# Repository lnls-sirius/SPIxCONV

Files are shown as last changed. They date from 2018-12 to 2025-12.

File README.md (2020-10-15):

# SPIxCONV

This project consists of an 18-bit analog input (ADC) and output (DAC) within a range of 20 V (± 10 V) and 32 digital pins that can be either as inputs or outputs. This system interfaces with pulsed power electronics hardware in order to control the output voltage for pulsed magnets as well as read and write status commands to their power supplies. An operator interface (OPI) software based on Qt was also developed for remote control.

<!--========================================-->
## Hardware
<!--========================================-->

<!--==============================-->
### Main Board
<!--==============================-->

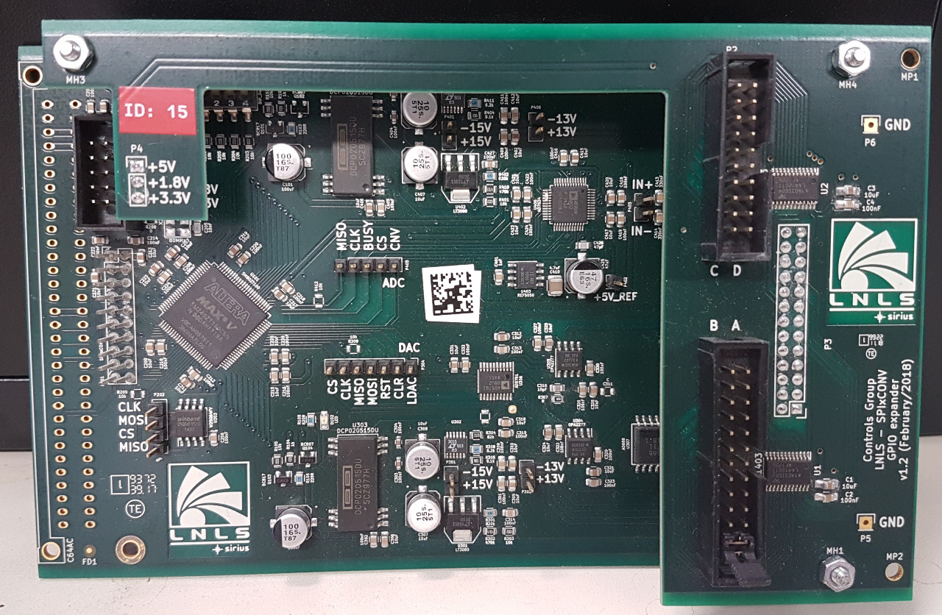
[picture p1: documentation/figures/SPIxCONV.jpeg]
Main Board


<!--====================-->
#### Circuit
<!--====================-->

  - Board
<p float="left">
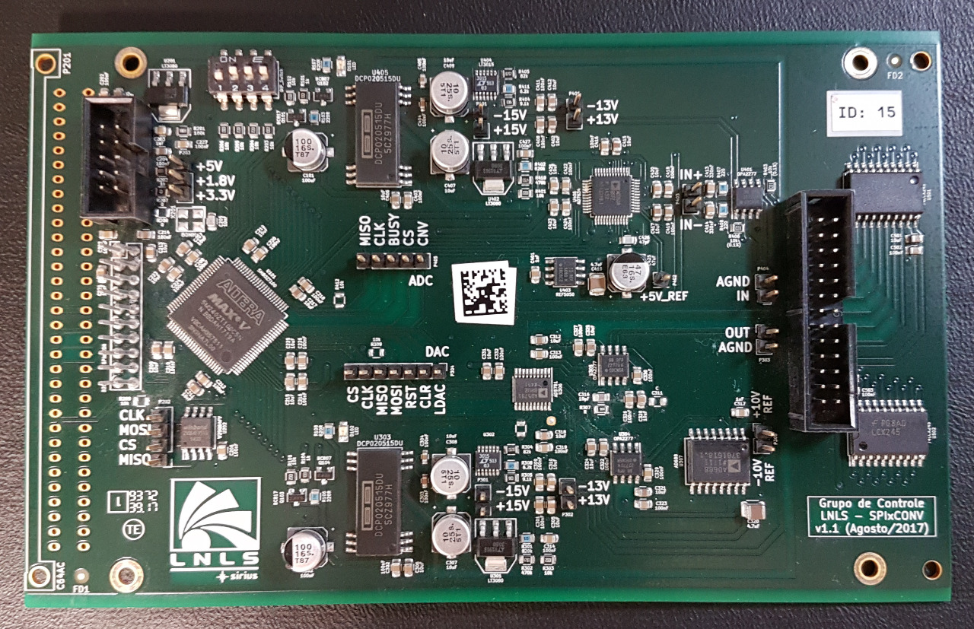
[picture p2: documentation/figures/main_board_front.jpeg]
  
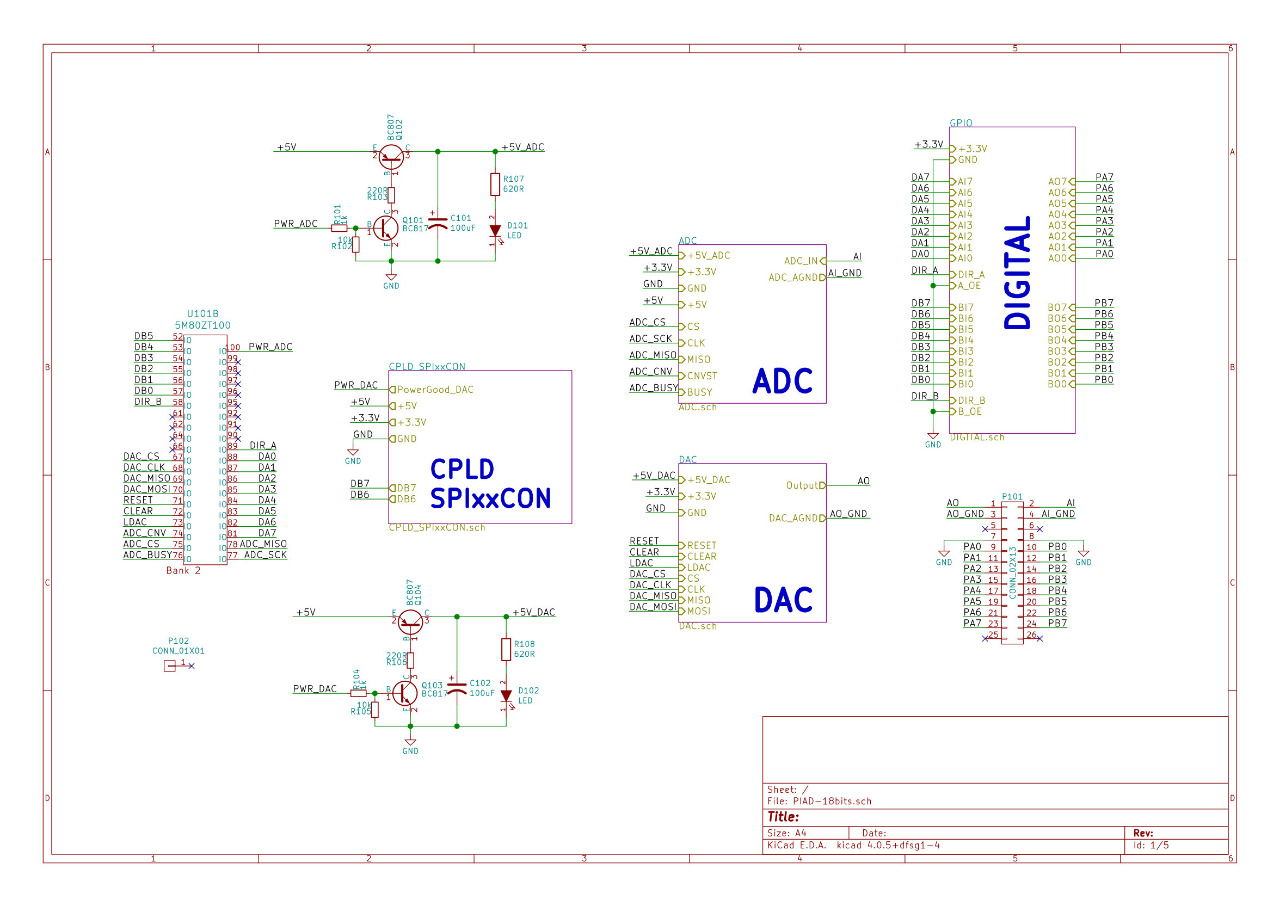
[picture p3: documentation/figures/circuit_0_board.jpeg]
   
</p>

  - CPLD
<p float="left">
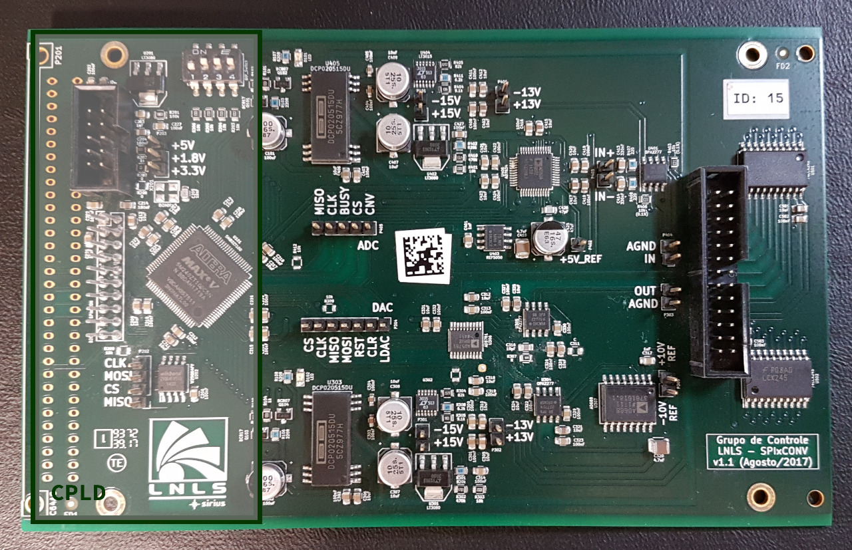
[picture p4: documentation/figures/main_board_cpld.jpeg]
  
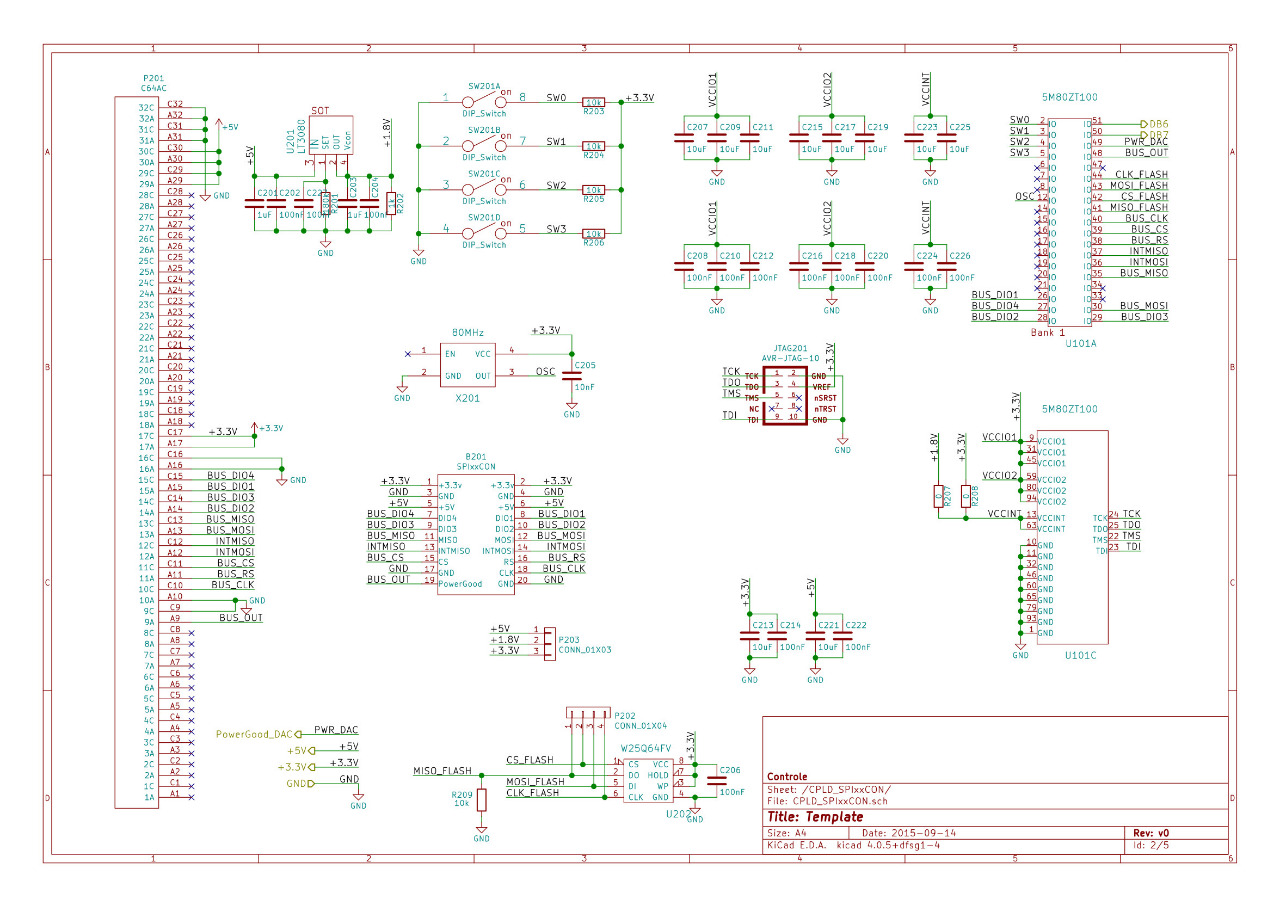
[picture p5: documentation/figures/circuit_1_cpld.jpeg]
   
</p>

  - DAC
<p float="left">
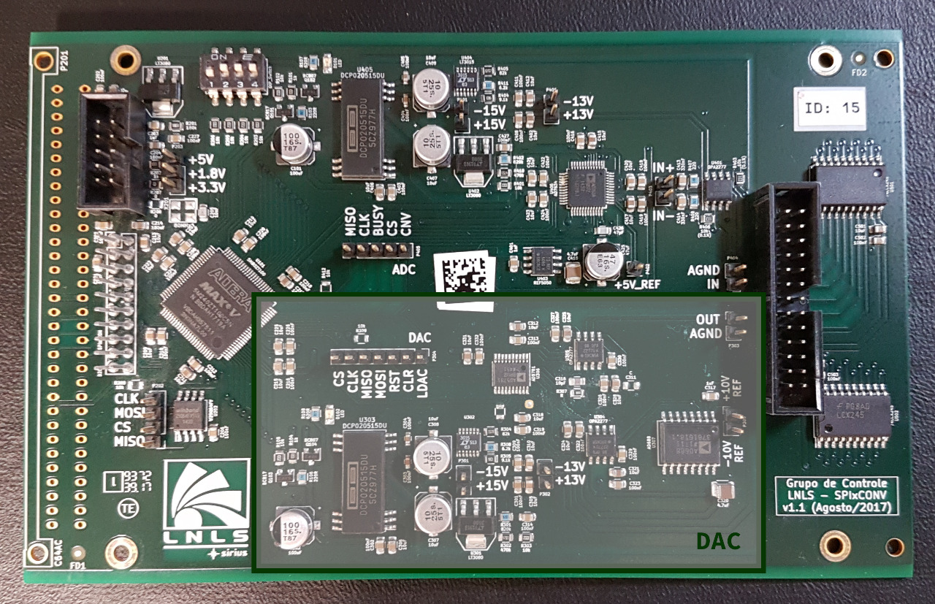
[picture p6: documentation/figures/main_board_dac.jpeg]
  
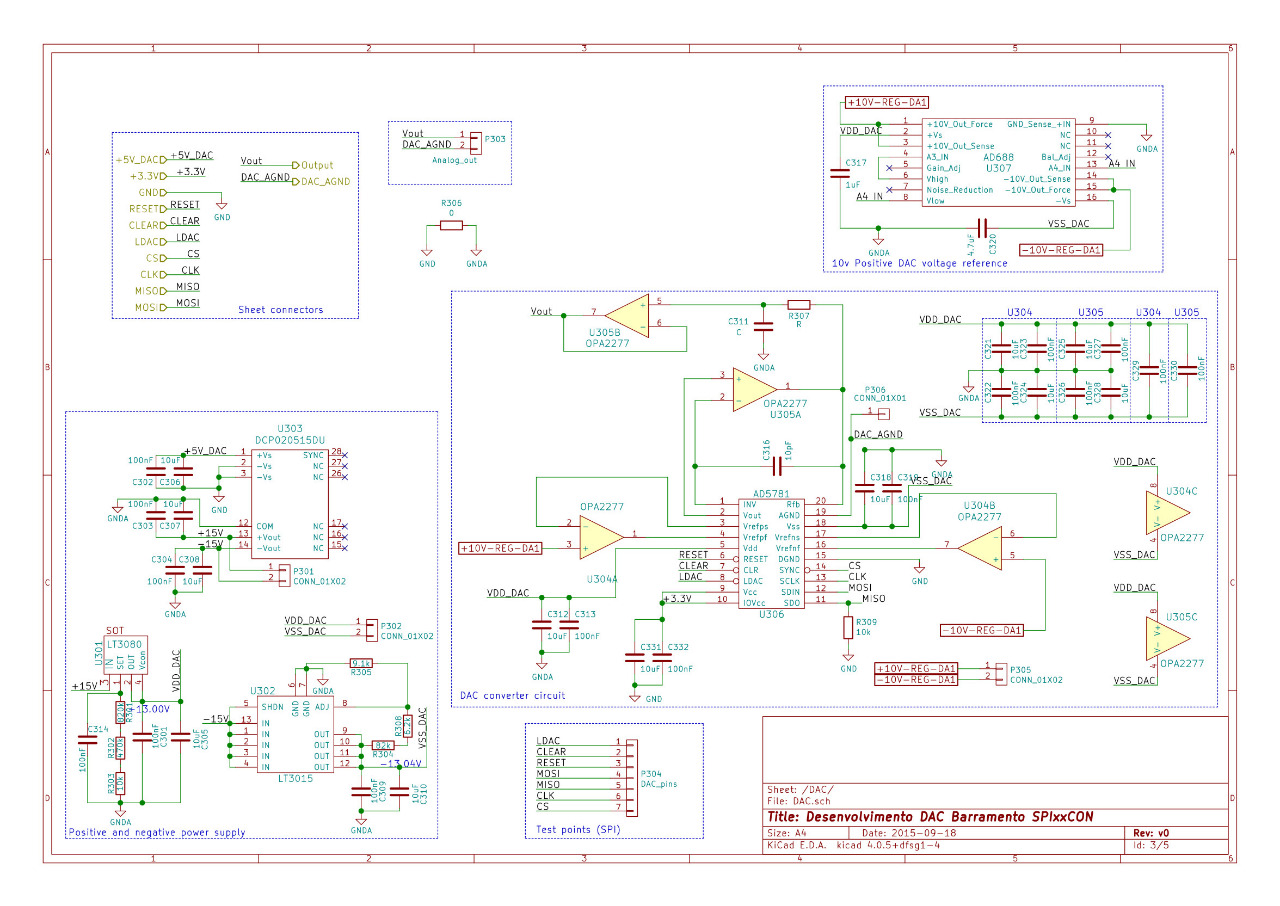
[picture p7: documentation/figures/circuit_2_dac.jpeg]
   
</p>

  - ADC
<p float="left">
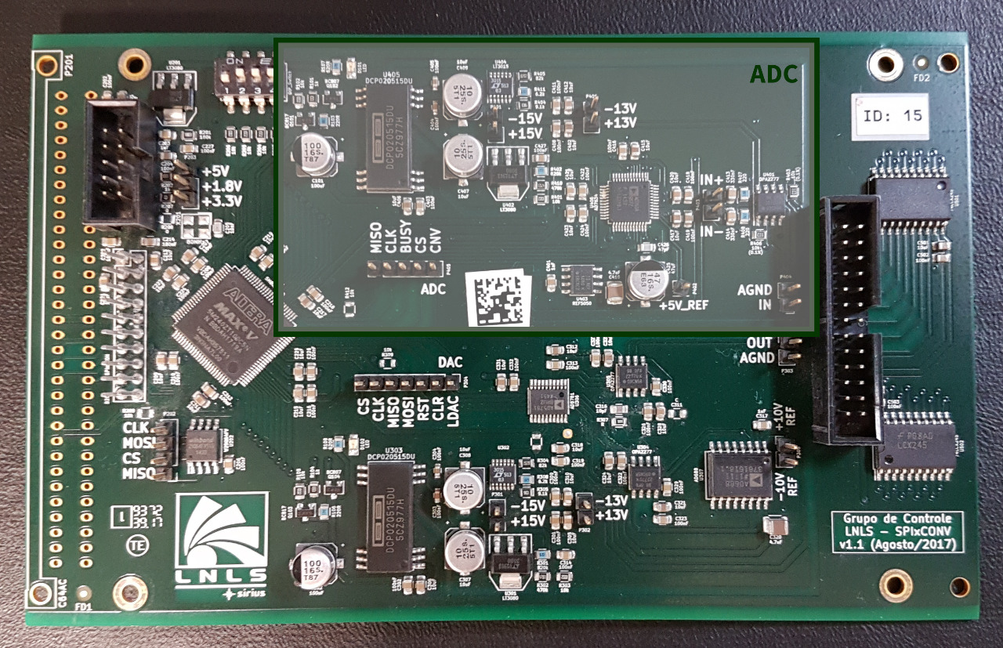
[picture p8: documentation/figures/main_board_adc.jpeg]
  
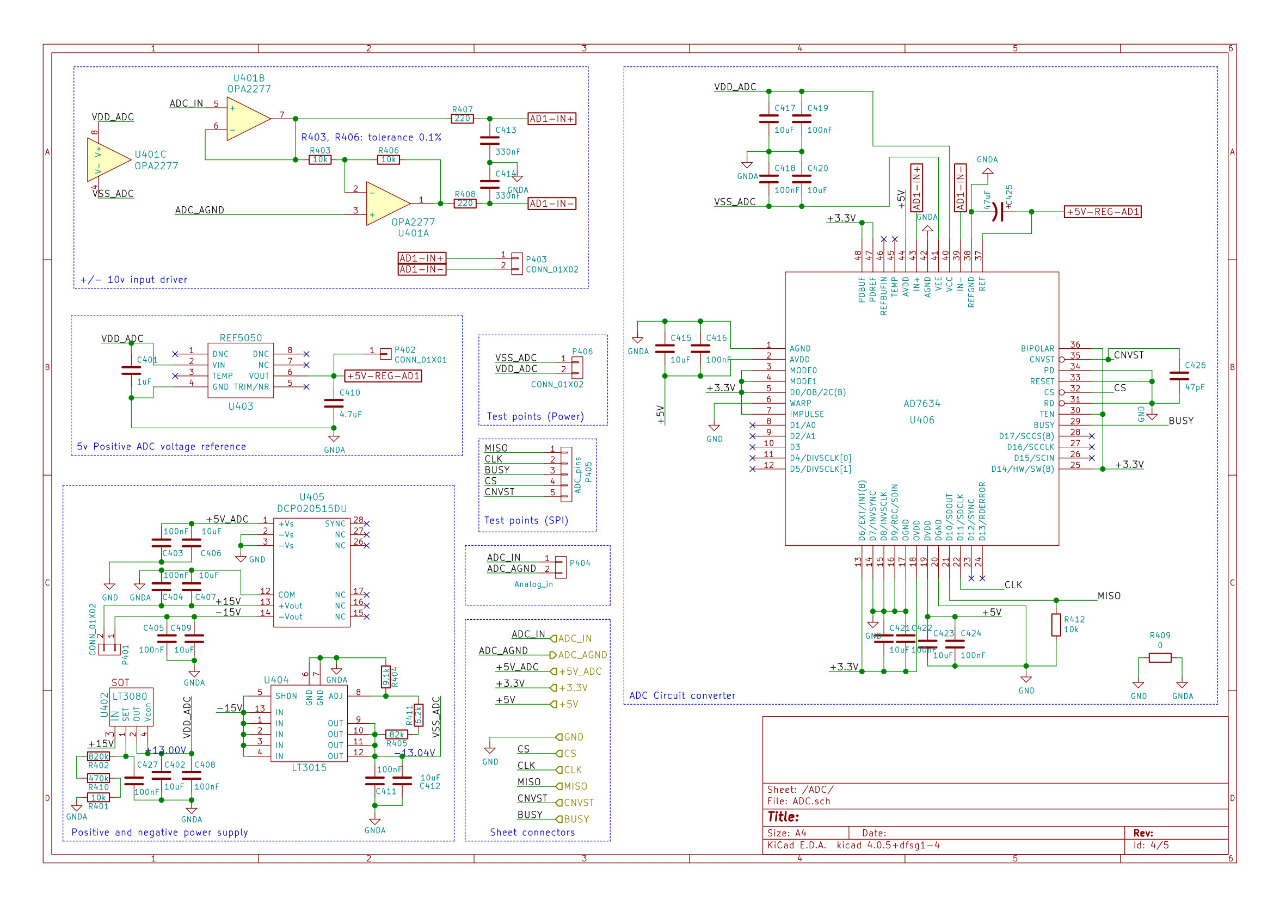
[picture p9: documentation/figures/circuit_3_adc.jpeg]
   
</p>

  - Digital I/O
<p float="left">
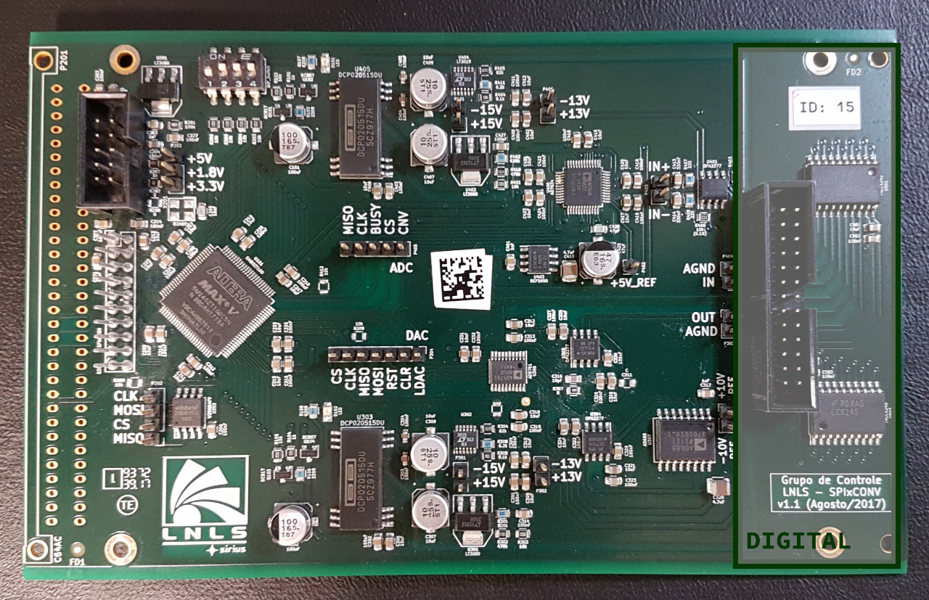
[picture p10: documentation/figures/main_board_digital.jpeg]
  
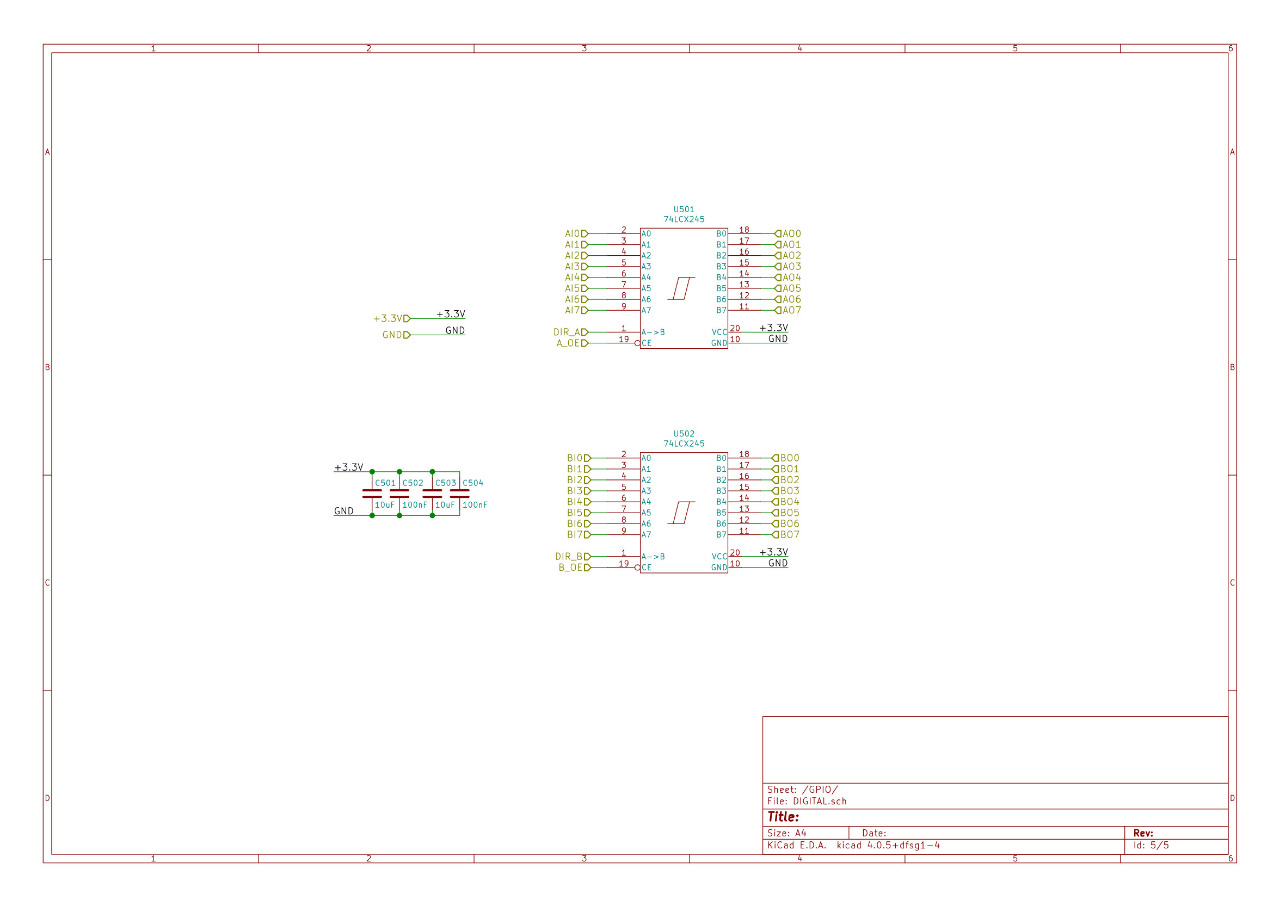
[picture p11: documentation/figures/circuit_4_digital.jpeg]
   
</p>

<!--====================-->
#### PCB
<!--====================-->

<p float="left">
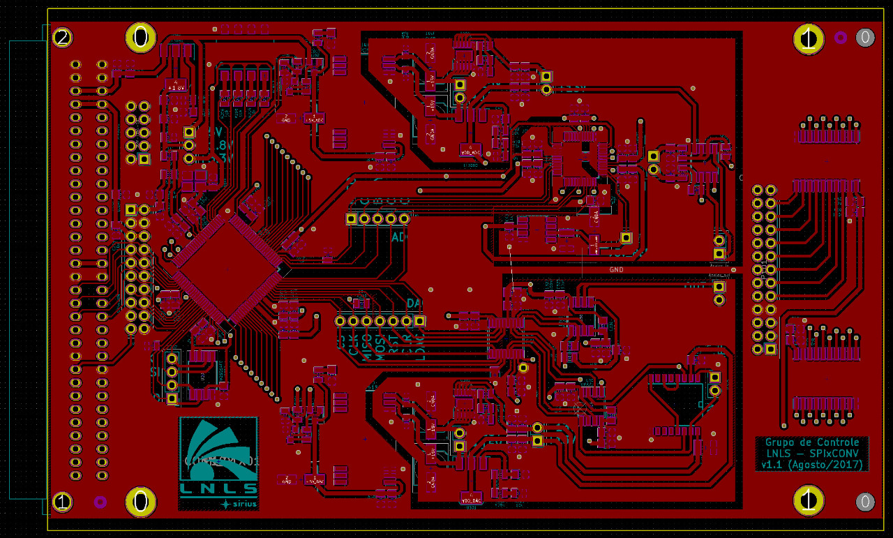
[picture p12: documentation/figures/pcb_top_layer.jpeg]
   
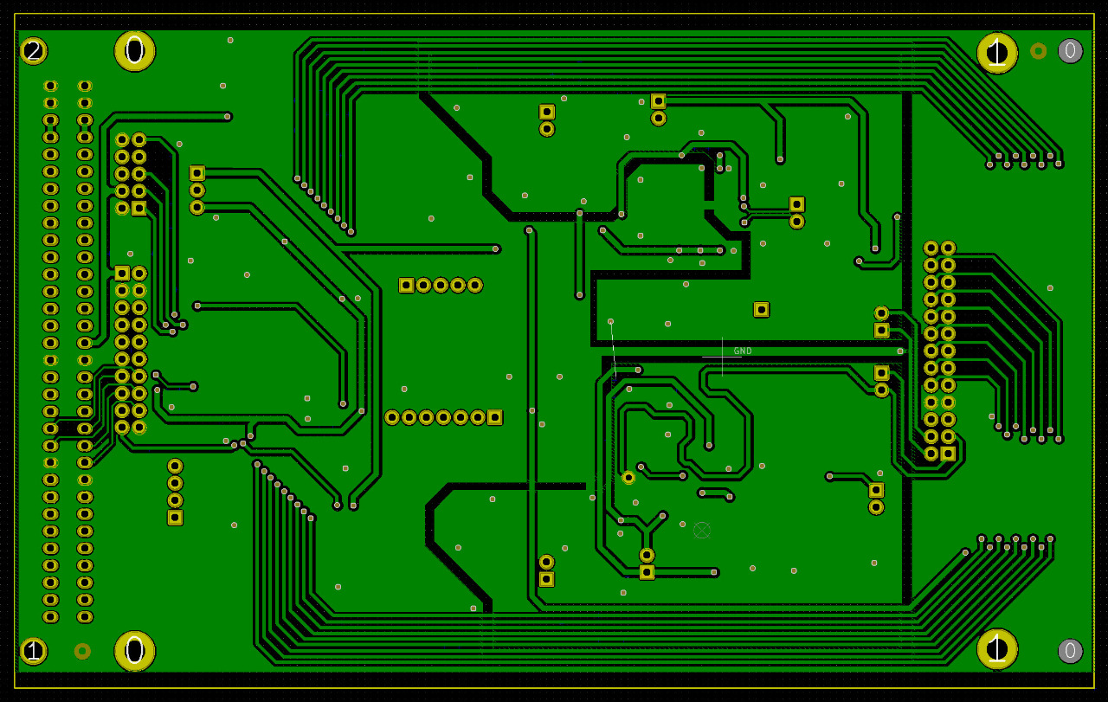
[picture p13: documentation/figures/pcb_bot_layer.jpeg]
  
</p>

<!--====================-->
#### Connectors
<!--====================-->

  - SPIxxCON
<p float="left">
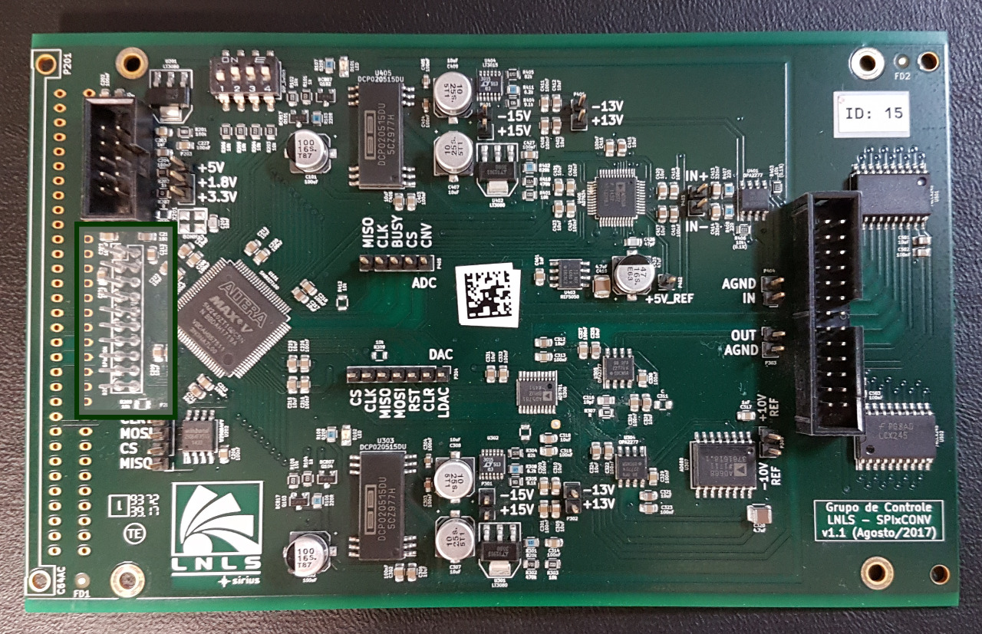
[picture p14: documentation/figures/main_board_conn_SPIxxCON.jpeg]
   
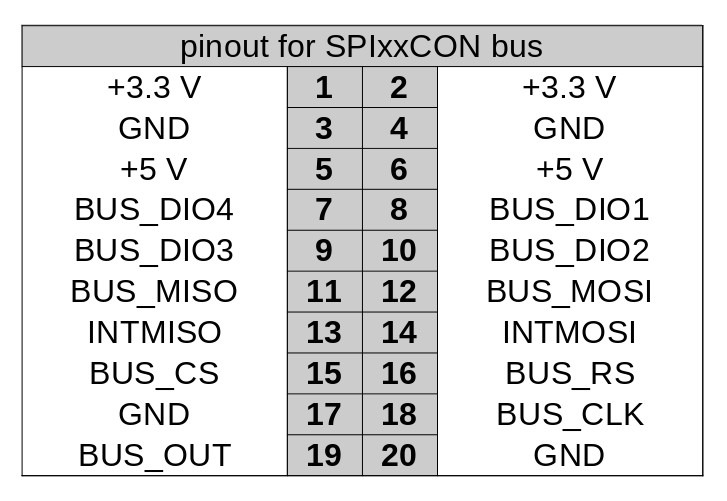
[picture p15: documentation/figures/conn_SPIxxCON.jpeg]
  
</p>

  - CPLD
<p float="left">
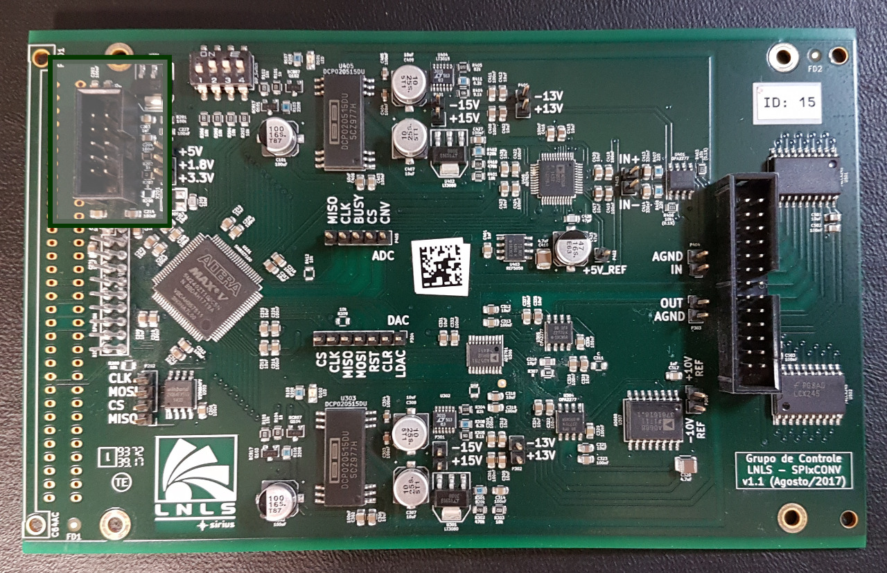
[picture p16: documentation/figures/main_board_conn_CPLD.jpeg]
   
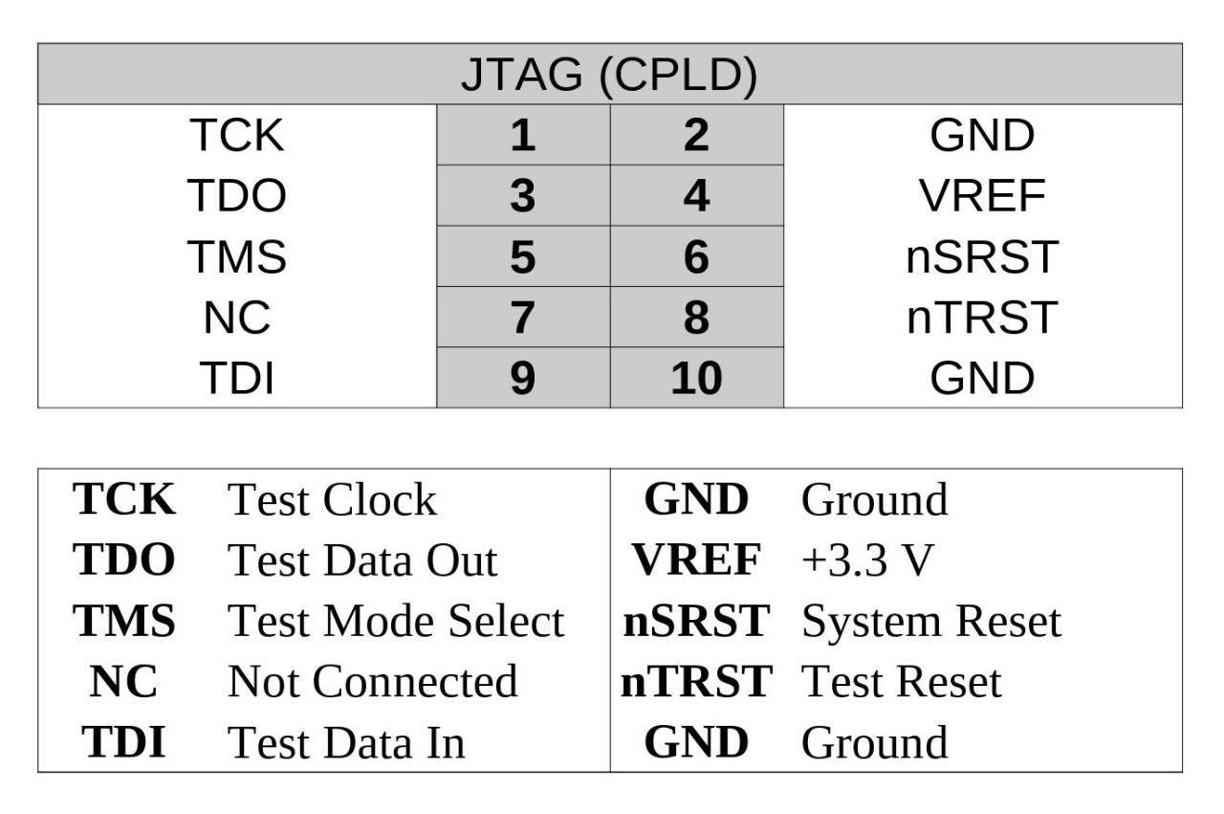
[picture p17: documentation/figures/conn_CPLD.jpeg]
  
</p>

  - Board Connection Link
<p float="left">
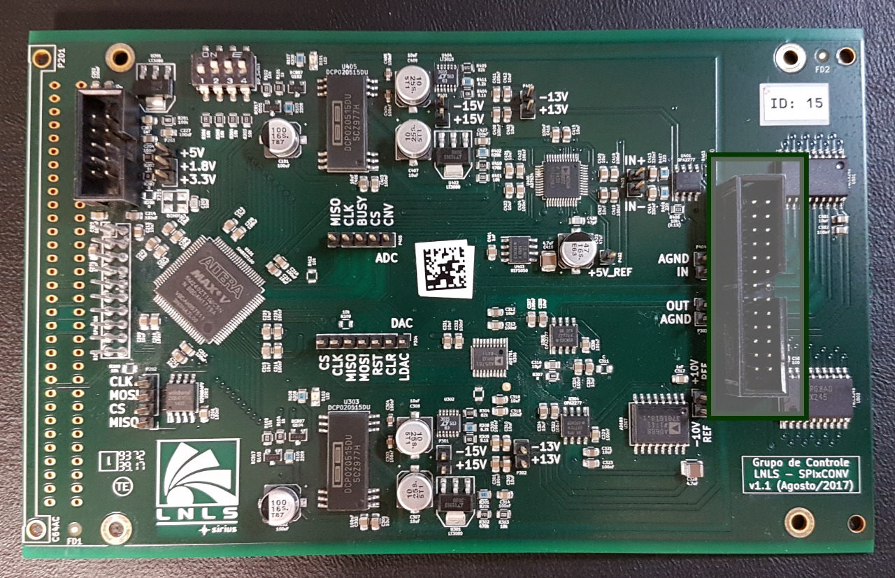
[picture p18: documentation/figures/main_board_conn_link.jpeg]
   
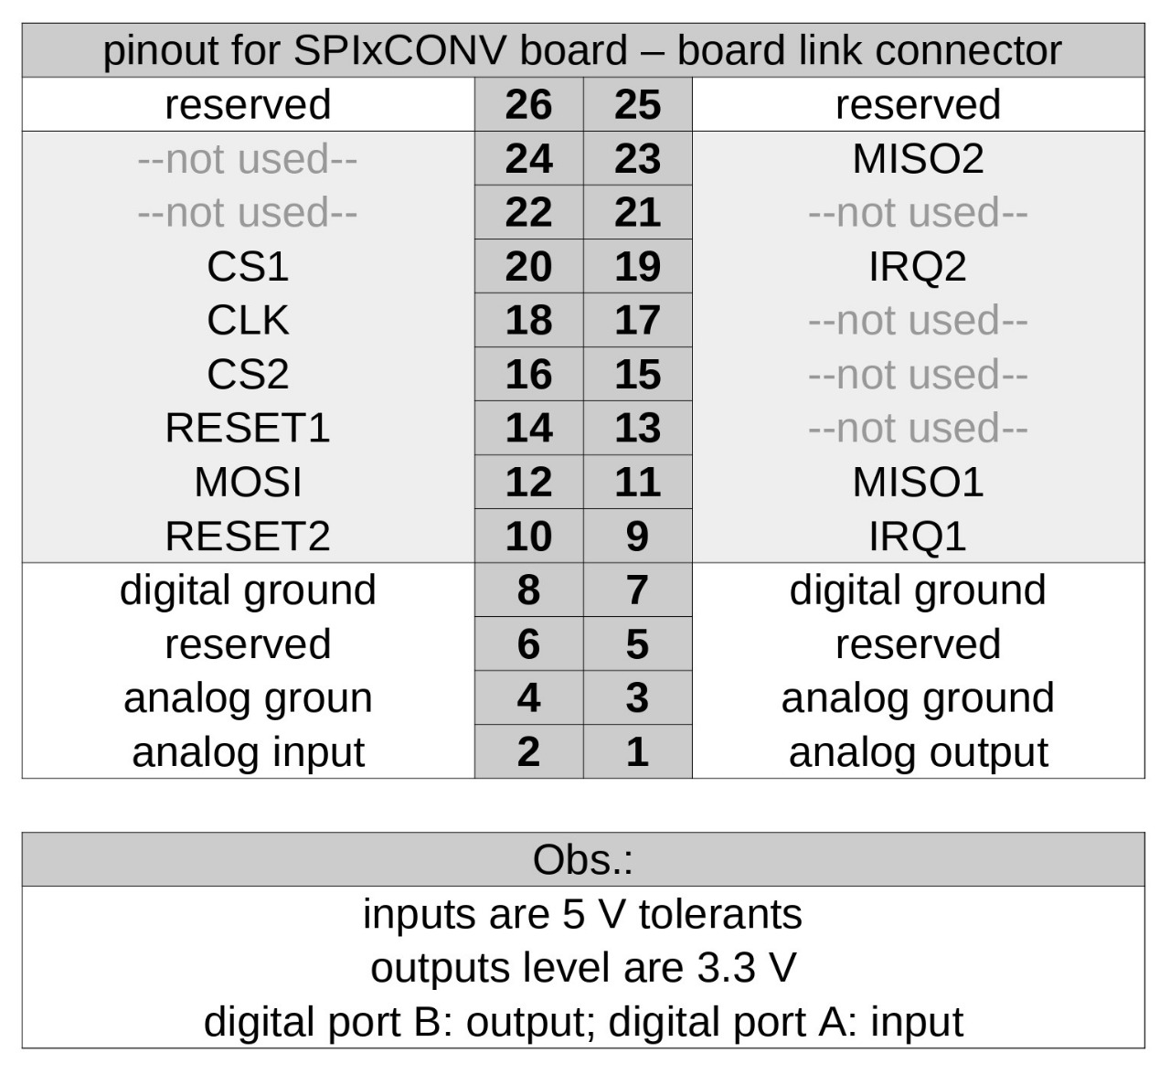
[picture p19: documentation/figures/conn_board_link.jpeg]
  
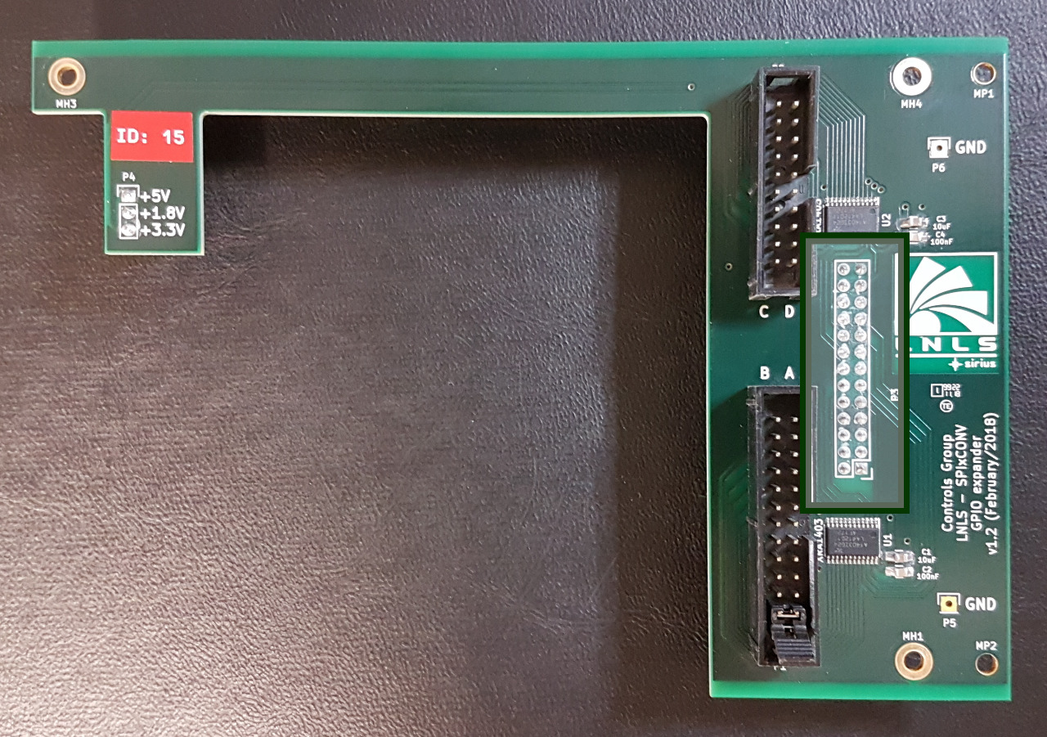
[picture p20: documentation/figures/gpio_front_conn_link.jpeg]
  
</p>

<!--====================-->
#### Test Points
<!--====================-->

  - SPI
<p float="left">
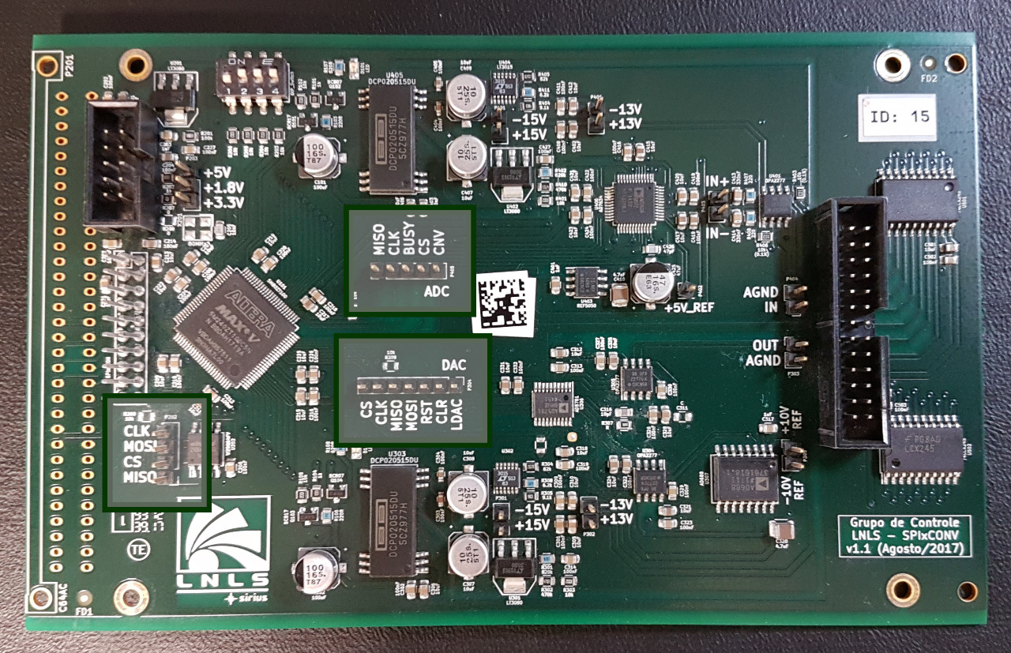
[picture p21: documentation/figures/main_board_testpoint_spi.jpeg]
  
</p>

  - Power Voltage
<p float="left">
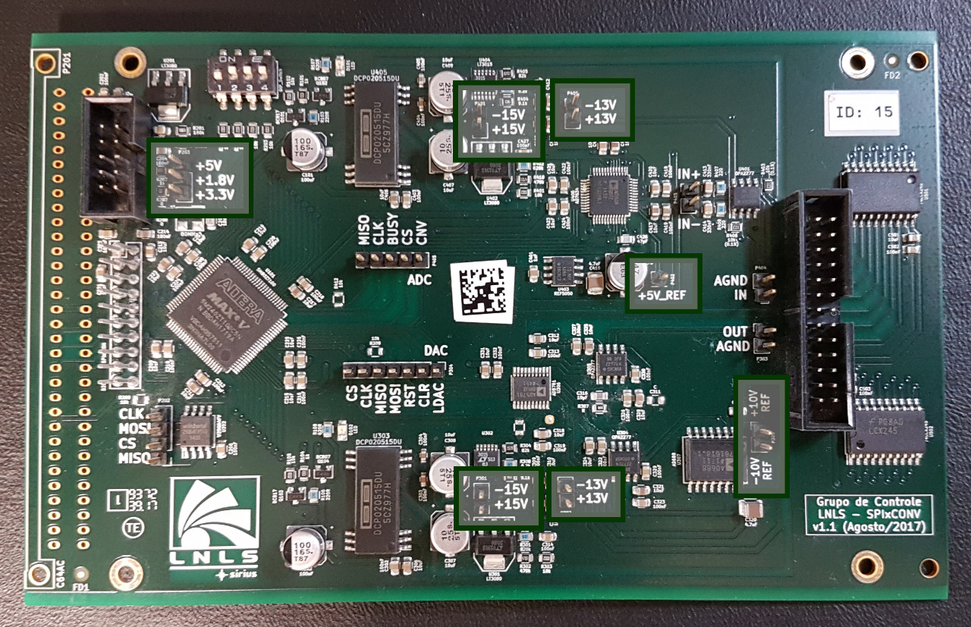
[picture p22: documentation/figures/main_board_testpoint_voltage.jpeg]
  
</p>

  - Analog In/Out
<p float="left">
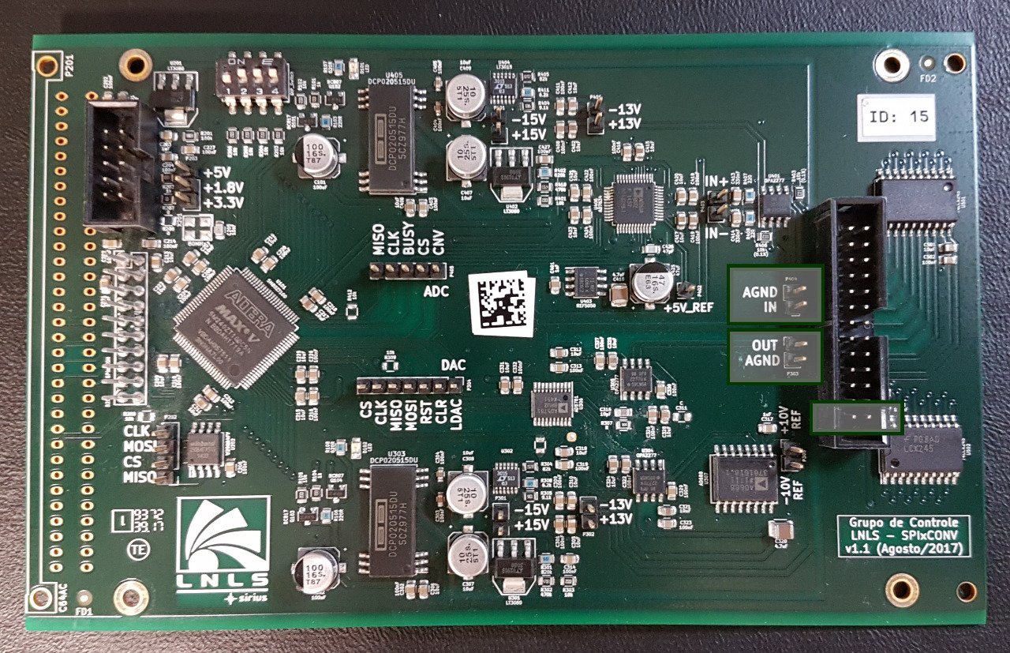
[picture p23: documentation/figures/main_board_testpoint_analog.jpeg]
  
</p>

<!--====================-->
#### BOM
<!--====================-->
Bill of materials

<!--==============================-->
### GPIO Expander Board
<!--==============================-->

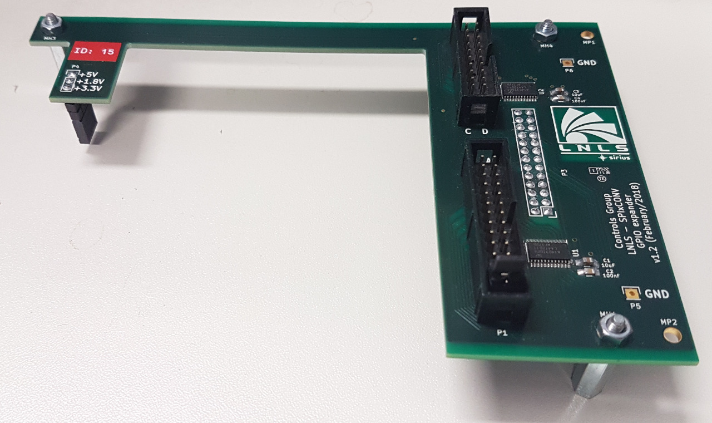
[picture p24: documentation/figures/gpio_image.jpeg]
GPIO Expander Board


<!--====================-->
#### Circuit
<!--====================-->
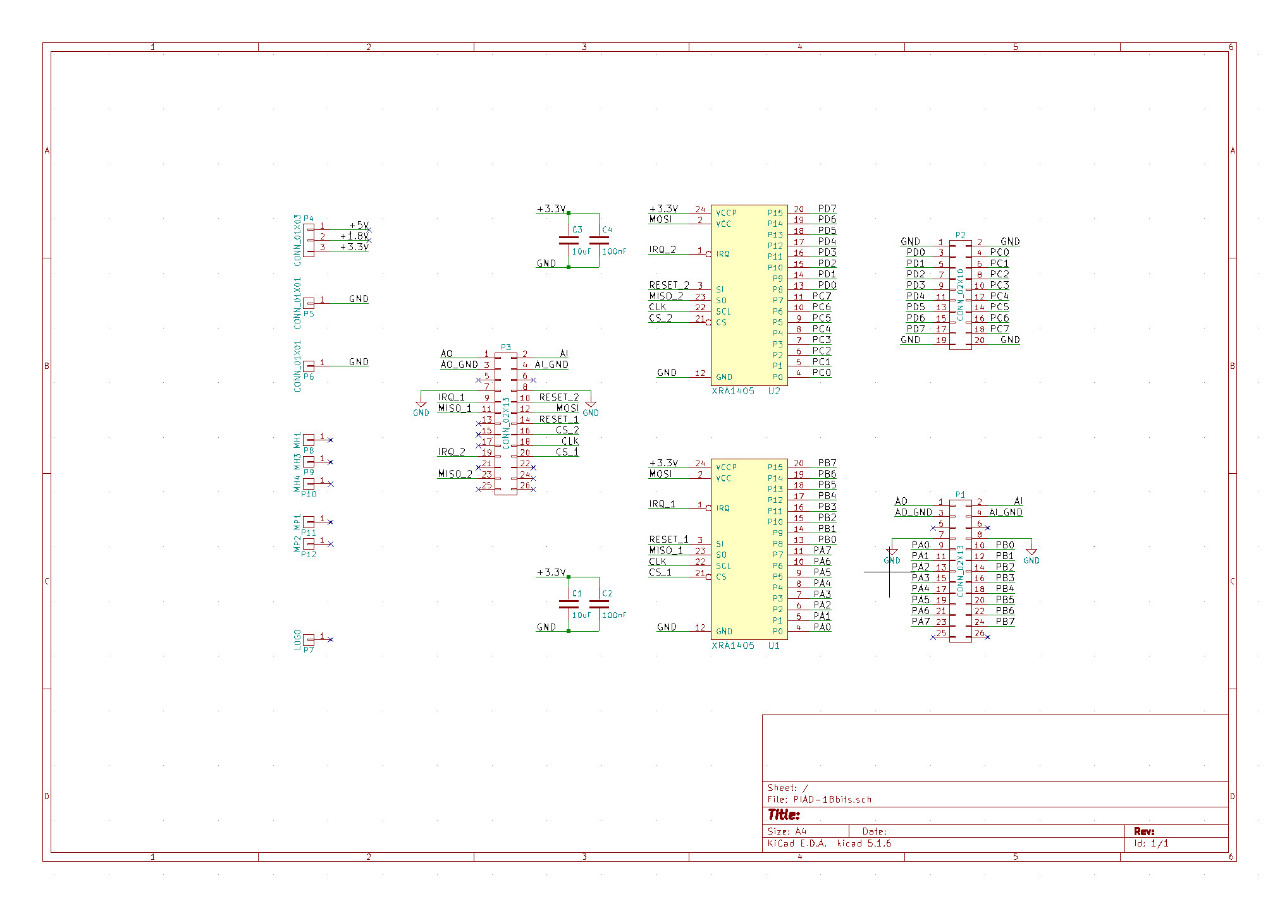
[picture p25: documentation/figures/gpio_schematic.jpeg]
GPIO board circuit


<!--====================-->
#### PCB
<!--====================-->
<p float="left">
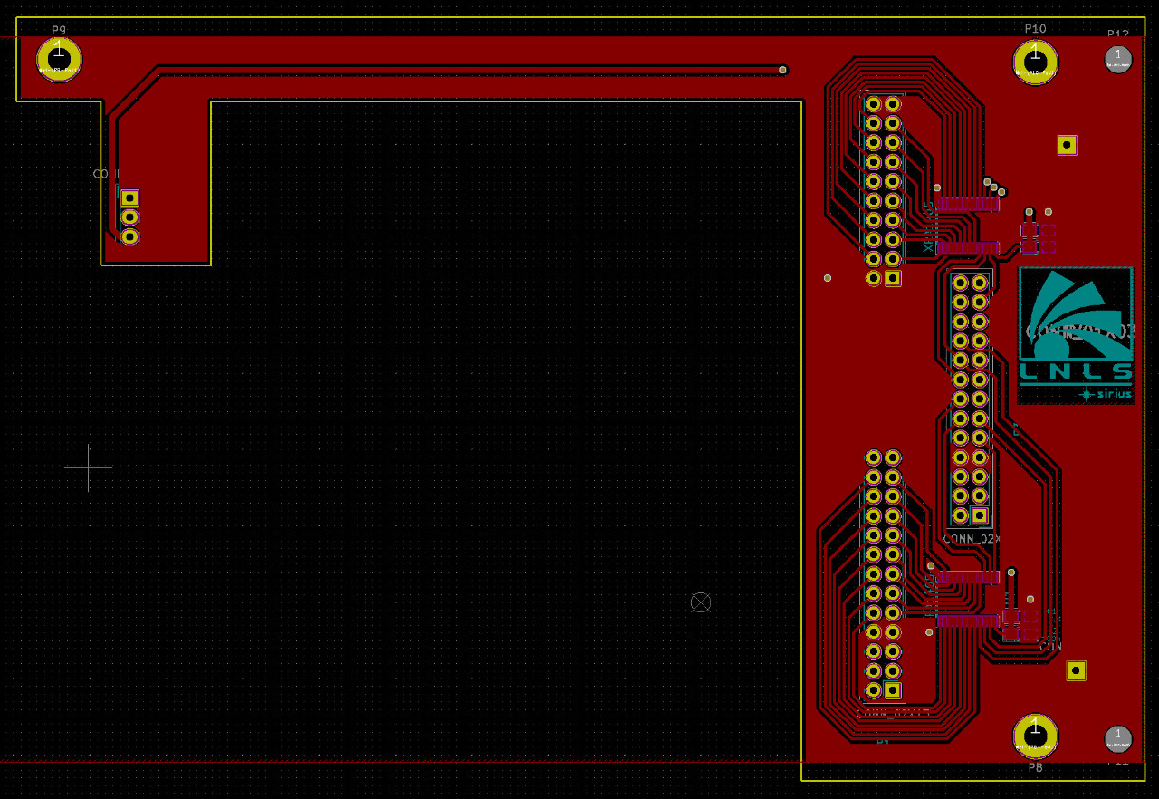
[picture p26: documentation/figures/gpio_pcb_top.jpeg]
   
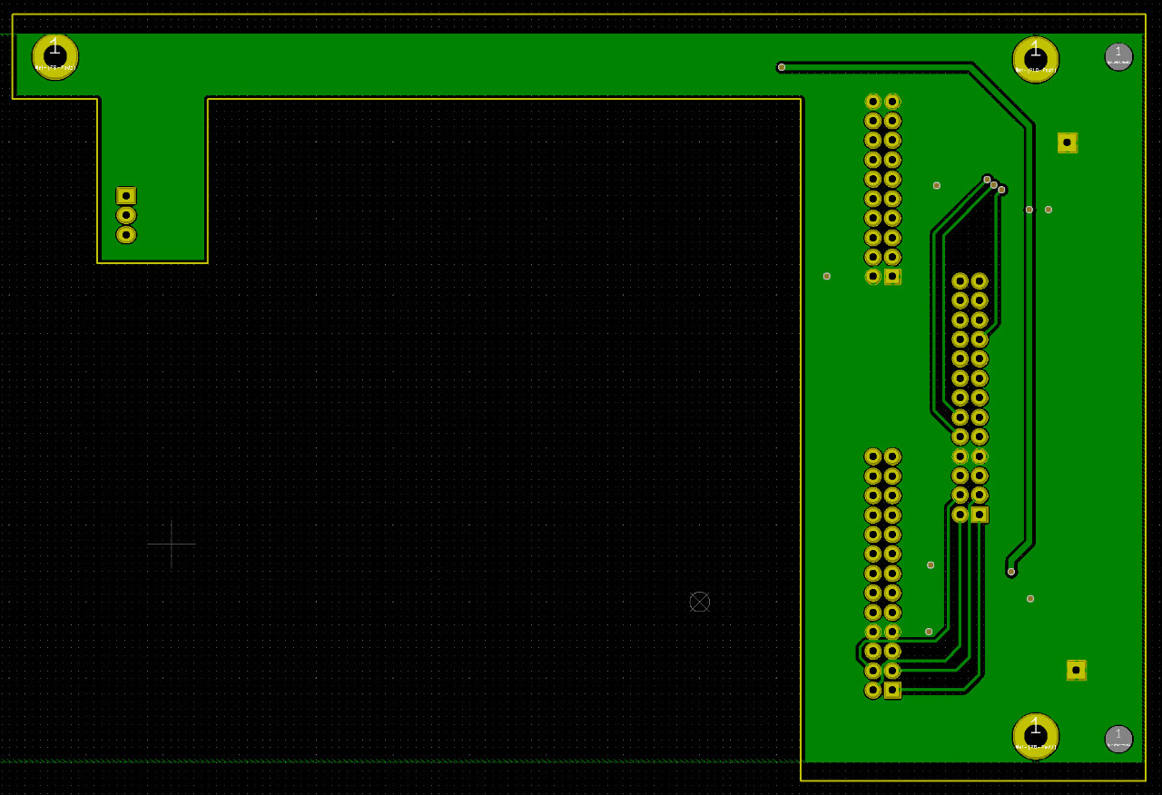
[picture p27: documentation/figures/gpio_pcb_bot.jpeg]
  
</p>

<!--====================-->
#### Connectors
<!--====================-->

  - Interface A/B
<p float="left">
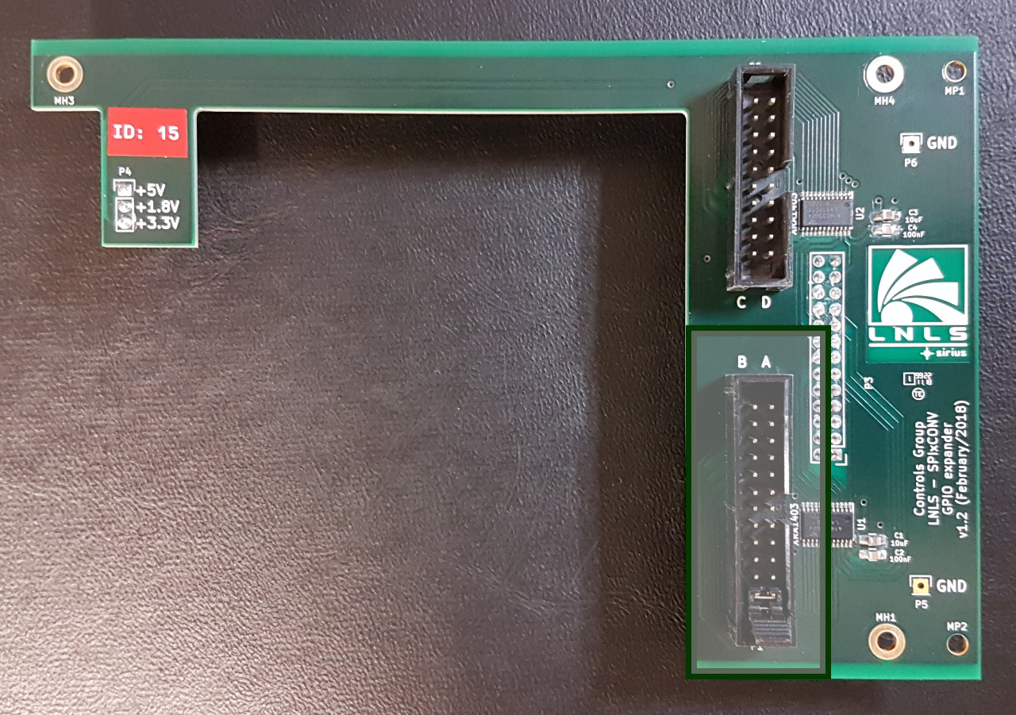
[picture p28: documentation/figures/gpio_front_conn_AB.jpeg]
   
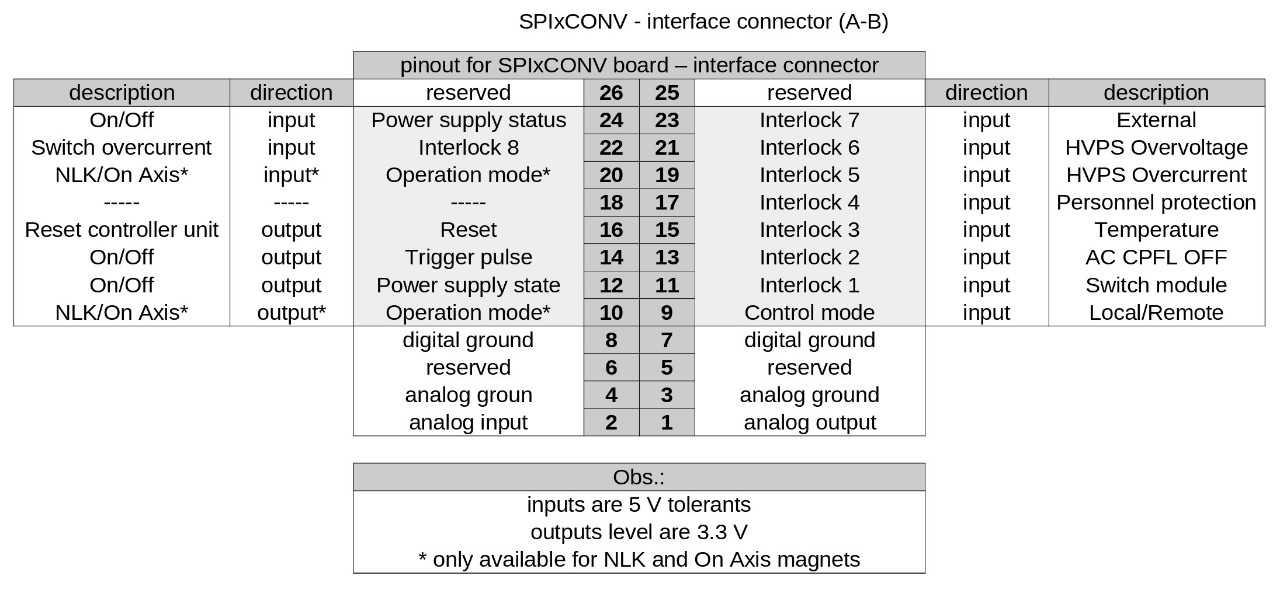
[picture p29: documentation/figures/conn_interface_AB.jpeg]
  
</p>

  - Interface C/D
<p float="left">
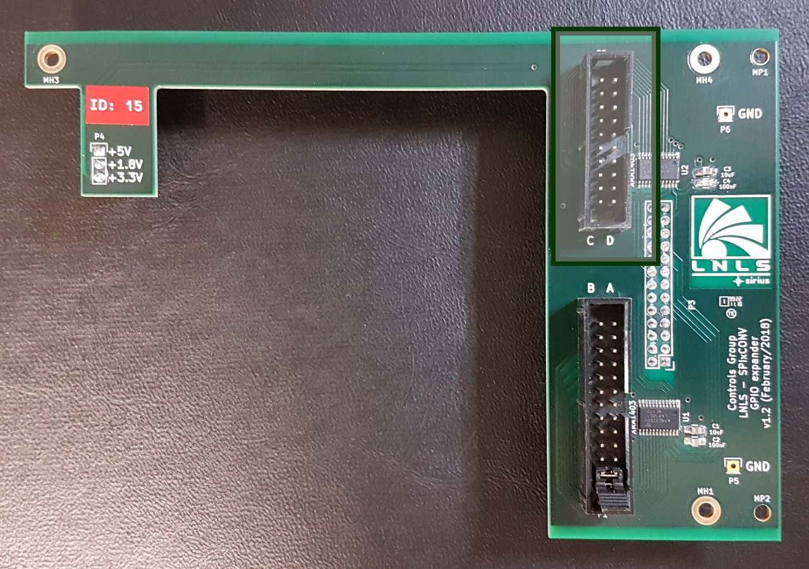
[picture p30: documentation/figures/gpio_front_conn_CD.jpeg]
   
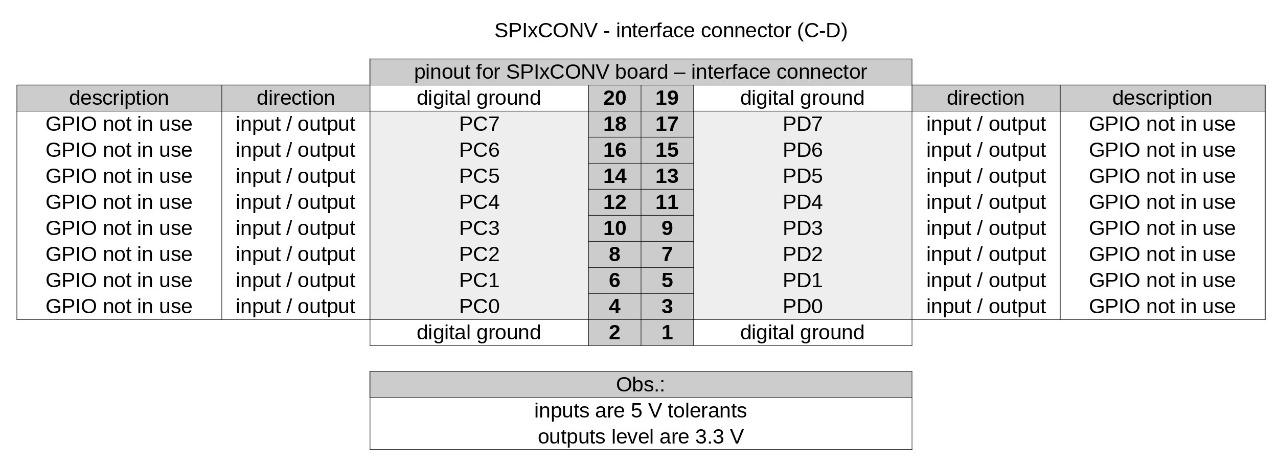
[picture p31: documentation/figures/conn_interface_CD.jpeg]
  
</p>

<!--====================-->
#### Test Points
<!--====================-->

  - Power Voltage
<p float="left">
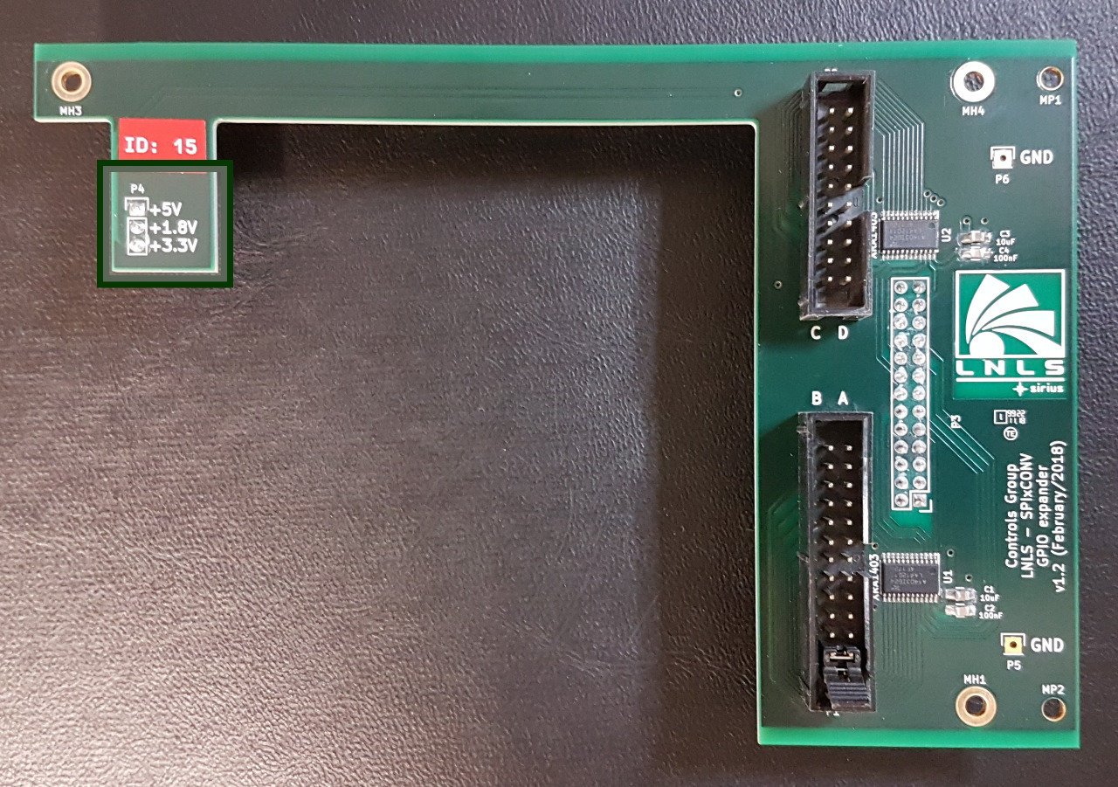
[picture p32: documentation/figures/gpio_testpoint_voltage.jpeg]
  
</p>

  - Analog In/Out
<p float="left">
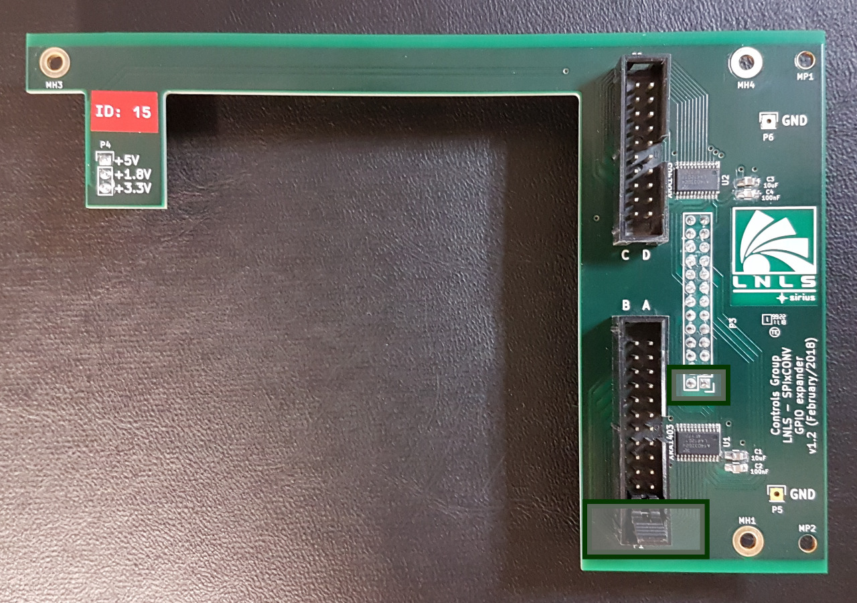
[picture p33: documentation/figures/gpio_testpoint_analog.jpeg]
  
</p>

<!--====================-->
#### BOM
<!--====================-->
Bill of materials

<!--====================-->
### Identification
<!--====================-->
<p float="left">
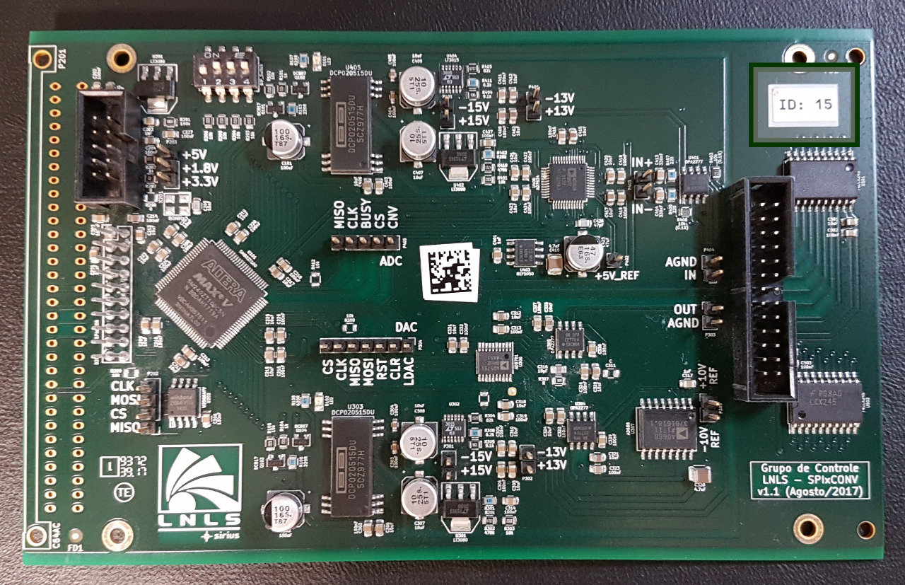
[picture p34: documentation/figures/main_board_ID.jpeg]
   
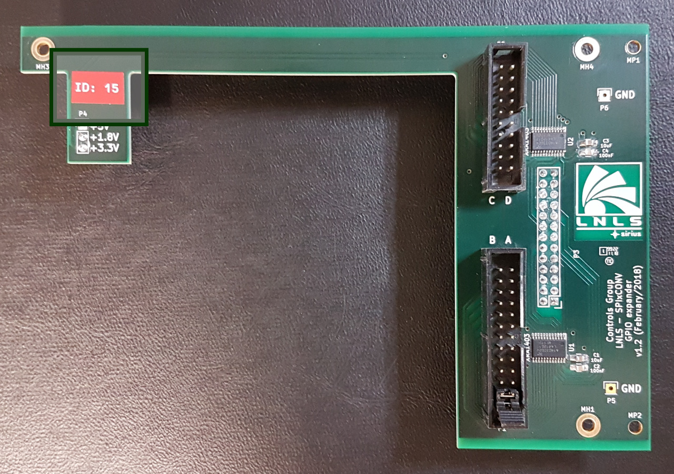
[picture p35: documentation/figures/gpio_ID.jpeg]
  
</p>

<!--========================================-->
### Software
<!--========================================-->

The software files of this project related to the server-side (IOC) is now available at [streamdevice-ioc](https://github.com/lnls-sirius/streamdevice-ioc) GitHub's repository under the "spixconv" directory.

The software files related to the OPI (Operator Interface) is now at [pydm-opi](https://github.com/lnls-sirius/pydm-opi) GitHub's repository.

Finally, the client-side (Python code) is at this repository under the [scripts](https://github.com/lnls-sirius/SPIxCONV/tree/master/software/scripts) directory.

<!--====================-->
#### Brief Description
<!--====================-->
To remotely control the board an [EPICS](https://epics-controls.org/about-epics/) IOC with an OPI was developed.

The IOC was built using [asynDriver](https://epics.anl.gov/modules/soft/asyn/) and [StreamDevice](http://epics.web.psi.ch/software/streamdevice/) on top of it. The application is launched in a form of a Docker container. The Docker image can be found at [Docker Hub](https://hub.docker.com/repository/docker/lnlscon/streamdevice-ioc) with the tag "SPIxCONV" followed by the version (eg: SPIxCONV-v1.9.6).

To configure the parameters of the IOC a [spreadsheet](https://cnpemcamp.sharepoint.com/:x:/s/controle/EUG0_4JUaz9Au7kZNcMZwZQB1x5OJBN_1QMdbbCGJ1Driw?e=Po8LNr) is used (available for CNPEM accounts only). PV's prefix, Power Supply voltage, host IP to connect to, scan rate and other settings can be adjusted. 

<!--====================-->
#### OPI (Operator Interface)
<!--====================-->

Previously, [Control System Studio](http://controlsystemstudio.org/) was used to develop the OPI. The windows can still be found under the [CSS](https://github.com/lnls-sirius/SPIxCONV/tree/master/software/CSS) directory. Lately, we have been using [PyDM (Python Display Manager)](https://slaclab.github.io/pydm/) to develop the windows. As stated before, the files related to the PyDM OPI is located in [pydm-opi](https://github.com/lnls-sirius/pydm-opi) repository.

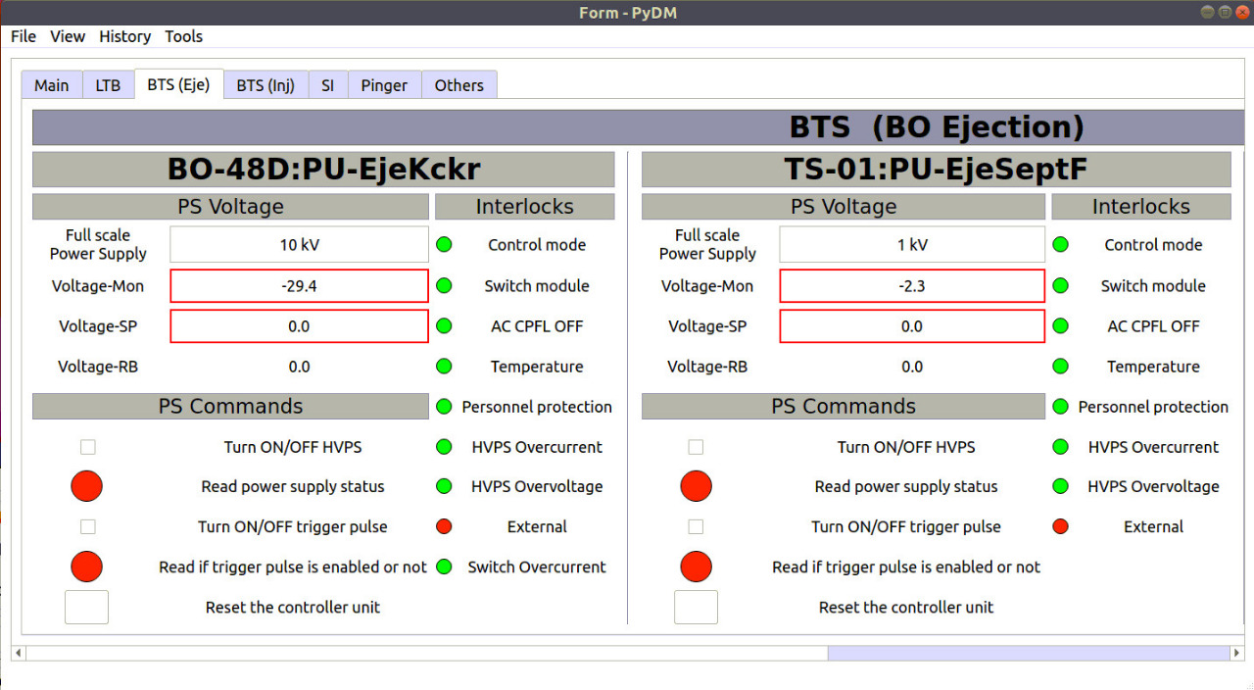
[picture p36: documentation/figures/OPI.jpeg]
OPI


<!--====================-->
#### CPLD
<!--====================-->

<p float="left">
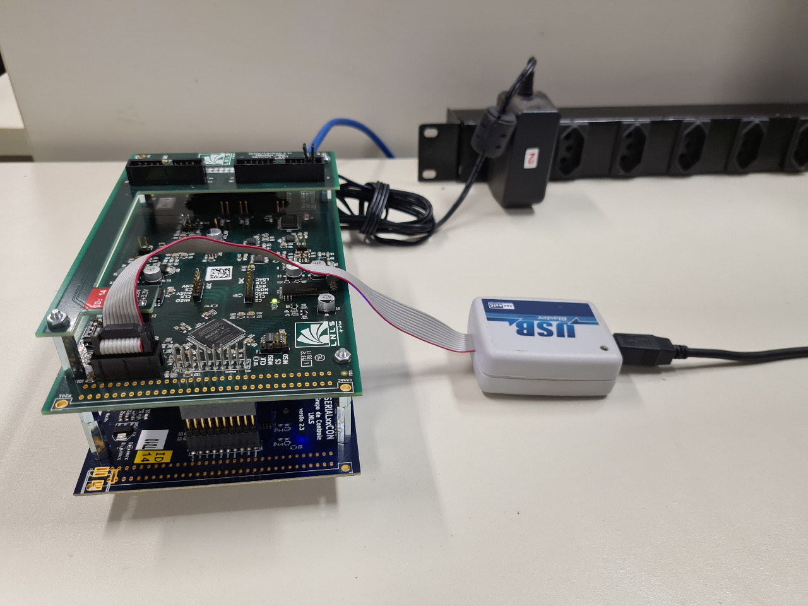
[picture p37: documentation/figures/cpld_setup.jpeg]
   
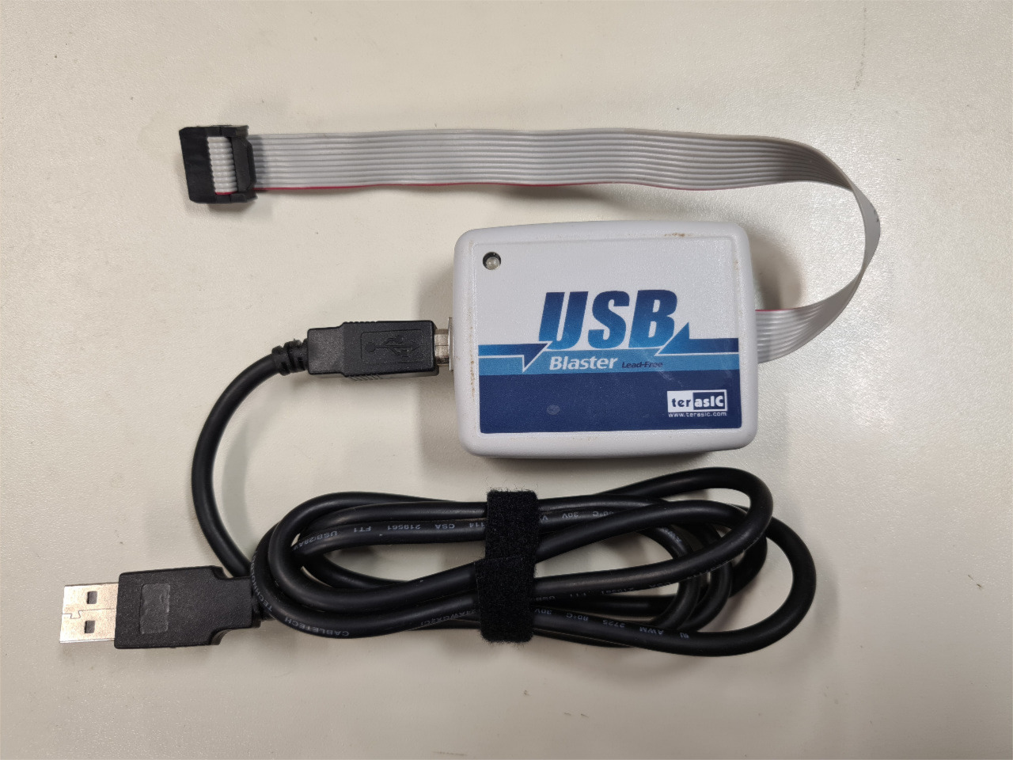
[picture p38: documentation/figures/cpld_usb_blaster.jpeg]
  
</p>

<!--====================-->
#### Board Calibration
<!--====================-->

To achieve more confiability, a calibration is done considering the DAC adjusts and the ADC measures. The next figures show the setup for this procedure. We basically connect the DAC output to the voltmeter and to the ADC input simultaneously.

<p float="left">
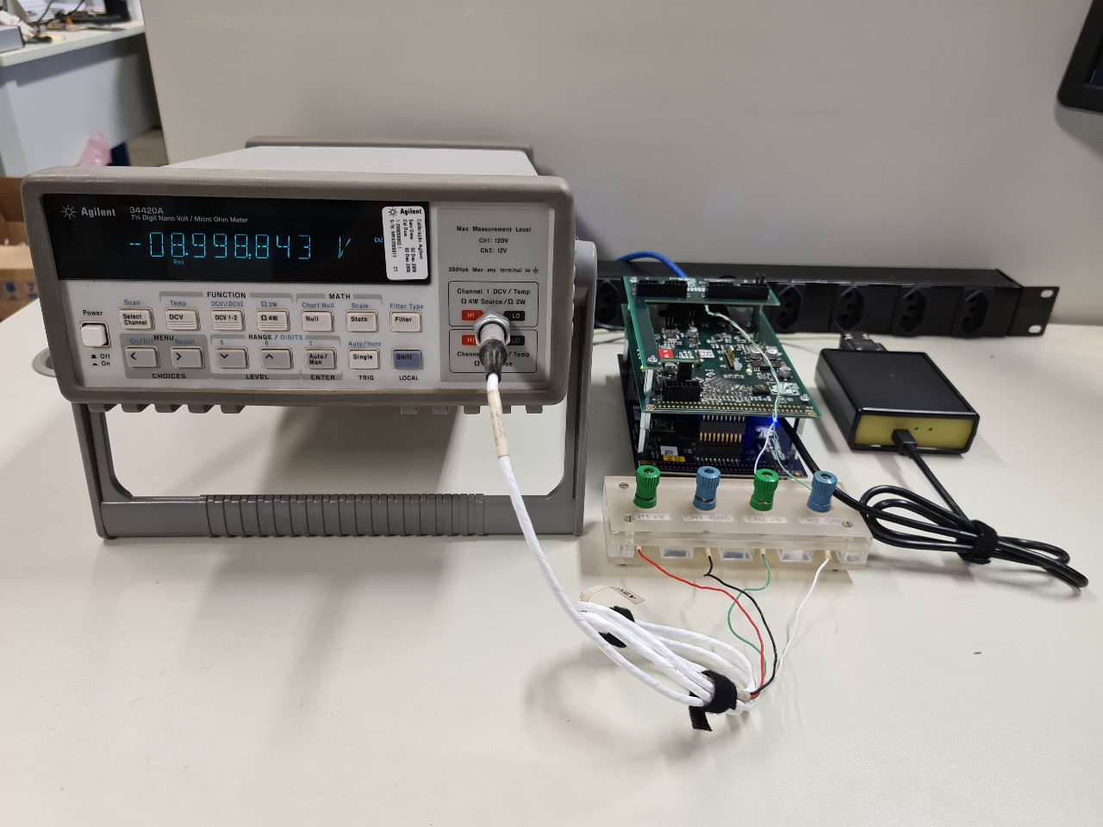
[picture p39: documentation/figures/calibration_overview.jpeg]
   
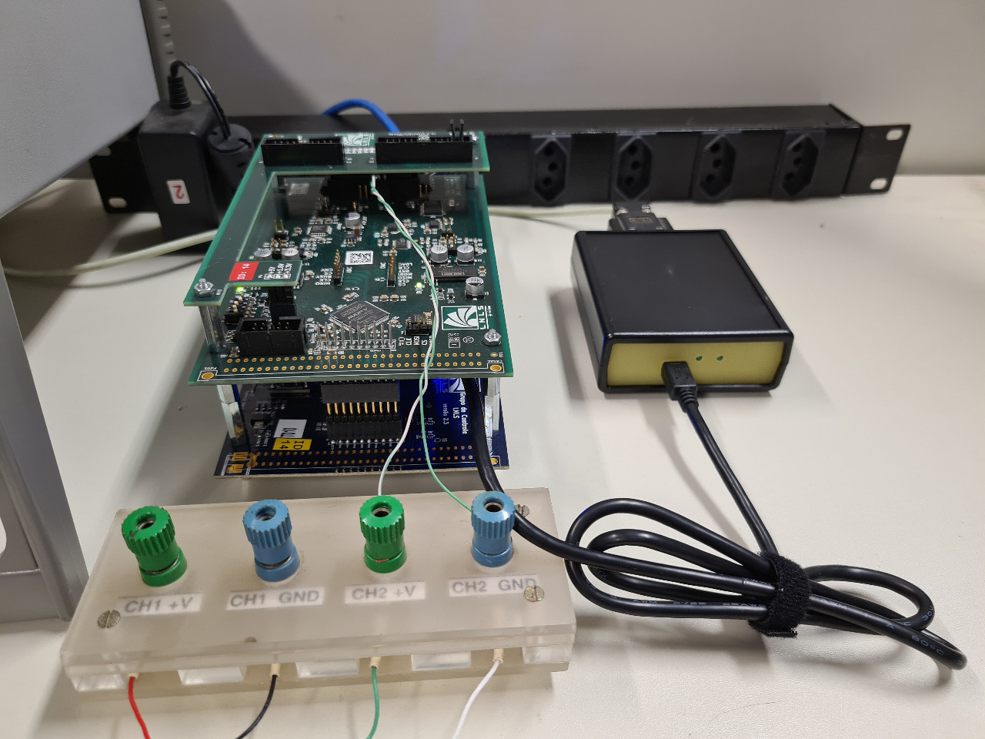
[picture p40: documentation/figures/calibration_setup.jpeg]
  
</p>

  - DAC calibration:
To calibrate the DAC we set its output to -9 V and later to +9 V and measure the real output voltage with the help of a 7 ½ digit voltmeter (here we are using the [Keysight 34420A](https://github.com/lnls-sirius/SPIxCONV/blob/master/documentation/Keysight%2034420A%20datasheet.pdf). We then use both measures to calculate the angular and linear coeffients for this curve.

  - ADC calibration:
Now that we have the DAC calibrated, we will use its output to calibrate the ADC coefficients. Again, we set the DAC output to -9 V (already considering the corrections), wait 60 s for thermal stabilization and read the voltage with the ADC. We then repeat the procedure for an adjustment of +9 V on the DAC output. Finally, these measures are used to calculate an angular and linear coefficient for the ADC.

An automated script was developed for this process. To control the voltmeter 34420A remotely we need a RS-232/USB adaptor to plug it in the USB connector of the BeagleBone Black. An important thing to note, is that the serial cable (RS-232) has an identification to show which side is the voltmeter's one and which should be connected to the adaptor.

<p float="left">
   
  
</p>

Finally, to calibrate the board, just connect to the BeagleBone Black and run the appropriate scrips, as showed below:

```console
$ ssh root@<BBB-IP>
root@beaglebone:~# systemctl stop bbb-function
root@beaglebone:~# /root/spixconv/software/scripts/calibration.py <BOARD-ID>
    gain = 1.00014284735
    offset = -15.81235112
    gain = 1.00052568324
    offset = -66.6829873034
```

Where <BBB-IP> is the BeagleBone IP (for example "192.168.7.2") and the <BOARD-ID> is the identification of the board (for example "15").

| Board ID |   DAC gain    |  DAC offset   |   ADC gain    |   ADC offset   |    Date    |
| :------: | :-----------: | :-----------: | :-----------: | :------------: | :--------: |
|     1    | 1.00022856796 | -23.604551795 | 1.00031151483 | -25.5034979525 | 06/14/2018 |
|     2    | 1.00026576963 | -28.880179670 | 1.00047415222 | -60.2158137830 | 06/14/2018 |
|     3    | 1.00030796599 | -32.699603180 | 1.00041814300 | -47.9227113769 | 06/18/2018 |
|     4    | 1.00017479634 | -17.242341185 | 1.00026390485 | -31.6174014794 | 06/19/2018 |
|     5    | 1.00017265115 | -13.974728690 | 1.00045784906 | -39.5533800101 | 06/19/2018 |
|     6    | 1.00015184443 | -11.674423865 | 1.00060158655 | -59.1729212883 | 06/19/2018 |
|     7    | 1.00019784934 | -20.918896760 | 1.00029330340 | -24.4439584471 | 06/19/2018 |
|     8    | 1.00035674834 | -37.769448800 | 1.00029168671 | -34.0324363824 | 06/19/2018 |
|     9    | 1.00023135812 | -26.566767695 | 1.00045023944 | -44.5911926966 | 06/19/2018 |
|    10    | 1.00020592482 | -21.571632830 | 1.00044201352 | -51.3525871959 | 06/19/2018 |
|    11    | 1.00014897135 | -16.862233835 | 1.00067934214 | -81.2456900362 | 06/19/2018 |
|    12    | 1.00022598345 | -22.008100925 | 1.00057691743 | -66.0110325831 | 06/19/2018 |
|    13    | 1.00032333122 | -33.267142775 | 1.00039023957 | -45.3552208747 | 06/19/2018 |
|    14    | 1.00016016368 | -18.311884625 | 1.00048566801 | -60.5575726483 | 06/19/2018 |
|    15    | 1.00022607238 | -22.051354520 | 1.00046470661 | -58.5770907625 | 06/19/2018 |
|    16    | 1.00028974958 | -32.626203140 | 1.00073037347 | -97.7370251289 | 06/19/2018 |
|    17    | 1.00027075563 | -27.292903805 | 1.00037276504 | -34.2682222150 | 06/20/2018 |
|    18    | 1.00017256223 | -15.753368945 | 1.00046720927 | -66.4461854942 | 06/20/2018 |
|    19    | 1.00023103020 | -24.296609315 | 1.00032961706 | -28.7417520711 | 06/20/2018 |
|    20    | 1.00019010191 | -20.998850375 | 1.00012983616 | -2.10309904365 | 06/20/2018 |

<!--====================-->
#### Code
<!--====================-->
[https://lnls-sirius.github.io/SPIxCONV/](https://lnls-sirius.github.io/SPIxCONV/)

<!--========================================-->
### Known Problems
<!--========================================-->

  - Not connecting to IOC after BBB reboots:  
    Status: both nodes (IOC and BBB) show they are connected, but the IOC does not respond.
    Solution: reboot IOC.

  - Flash memory loses data:
    Status: this happened once in three years. After a power cycle, the flash suddenly lost al its data!
    Solution: record information in flash memory again.

<!--========================================-->
### FAQ
<!--========================================-->

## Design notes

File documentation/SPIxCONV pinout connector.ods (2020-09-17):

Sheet: SPIxxCON bus
pinout for SPIxxCON bus
+3.3 V | 1 | 2 | +3.3 V
GND | 3 | 4 | GND
+5 V | 5 | 6 | +5 V
BUS_DIO4 | 7 | 8 | BUS_DIO1
BUS_DIO3 | 9 | 10 | BUS_DIO2
BUS_MISO | 11 | 12 | BUS_MOSI
INTMISO | 13 | 14 | INTMOSI
BUS_CS | 15 | 16 | BUS_RS
GND | 17 | 18 | BUS_CLK
BUS_OUT | 19 | 20 | GND

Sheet: JTAG (CPLD)
JTAG (CPLD)
TCK |  | 1 | 2 | GND
TDO |  | 3 | 4 | VREF
TMS |  | 5 | 6 | nSRST
NC |  | 7 | 8 | nTRST
TDI |  | 9 | 10 | GND
TCK | Test Clock |  | GND | Ground
TDO | Test Data Out |  | VREF | +3.3 V
TMS | Test Mode Select |  | nSRST | System Reset
NC | Not Connected |  | nTRST | Test Reset
TDI | Test Data In |  | GND | Ground

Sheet: SPIxCONV - board link connector
pinout for SPIxCONV board – board link connector
reserved | 26 | 25 | reserved
--not used-- | 24 | 23 | MISO2
--not used-- | 22 | 21 | --not used--
CS1 | 20 | 19 | IRQ2
CLK | 18 | 17 | --not used--
CS2 | 16 | 15 | --not used--
RESET1 | 14 | 13 | --not used--
MOSI | 12 | 11 | MISO1
RESET2 | 10 | 9 | IRQ1
digital ground | 8 | 7 | digital ground
reserved | 6 | 5 | reserved
analog groun | 4 | 3 | analog ground
analog input | 2 | 1 | analog output
Obs.:
inputs are 5 V tolerants
outputs level are 3.3 V
digital port B: output; digital port A: input

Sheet: SPIxCONV - interface connector (A-B)
 |  | pinout for SPIxCONV board – interface connector
description | direction | reserved | 26 | 25 | reserved | direction | description
On/Off | input | Power supply status | 24 | 23 | Interlock 7 | input | External
Switch overcurrent | input | Interlock 8 | 22 | 21 | Interlock 6 | input | HVPS Overvoltage
NLK/On Axis* | input* | Operation mode* | 20 | 19 | Interlock 5 | input | HVPS Overcurrent
----- | ----- | ----- | 18 | 17 | Interlock 4 | input | Personnel protection
Reset controller unit | output | Reset | 16 | 15 | Interlock 3 | input | Temperature
On/Off | output | Trigger pulse | 14 | 13 | Interlock 2 | input | AC CPFL OFF
On/Off | output | Power supply state | 12 | 11 | Interlock 1 | input | Switch module
NLK/On Axis* | output* | Operation mode* | 10 | 9 | Control mode | input | Local/Remote
 |  | digital ground | 8 | 7 | digital ground
 |  | reserved | 6 | 5 | reserved
 |  | analog groun | 4 | 3 | analog ground
 |  | analog input | 2 | 1 | analog output
 |  | Obs.:
 |  | inputs are 5 V tolerants
 |  | outputs level are 3.3 V
 |  | * only available for NLK and On Axis magnets

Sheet: SPIxCONV - interface connector (C-D)
 |  | pinout for SPIxCONV board – interface connector
description | direction | digital ground | 20 | 19 | digital ground | direction | description
GPIO not in use | input / output | PC7 | 18 | 17 | PD7 | input / output | GPIO not in use
GPIO not in use | input / output | PC6 | 16 | 15 | PD6 | input / output | GPIO not in use
GPIO not in use | input / output | PC5 | 14 | 13 | PD5 | input / output | GPIO not in use
GPIO not in use | input / output | PC4 | 12 | 11 | PD4 | input / output | GPIO not in use
GPIO not in use | input / output | PC3 | 10 | 9 | PD3 | input / output | GPIO not in use
GPIO not in use | input / output | PC2 | 8 | 7 | PD2 | input / output | GPIO not in use
GPIO not in use | input / output | PC1 | 6 | 5 | PD1 | input / output | GPIO not in use
GPIO not in use | input / output | PC0 | 4 | 3 | PD0 | input / output | GPIO not in use
 |  | digital ground | 2 | 1 | digital ground
 |  | Obs.:
 |  | inputs are 5 V tolerants
 |  | outputs level are 3.3 V

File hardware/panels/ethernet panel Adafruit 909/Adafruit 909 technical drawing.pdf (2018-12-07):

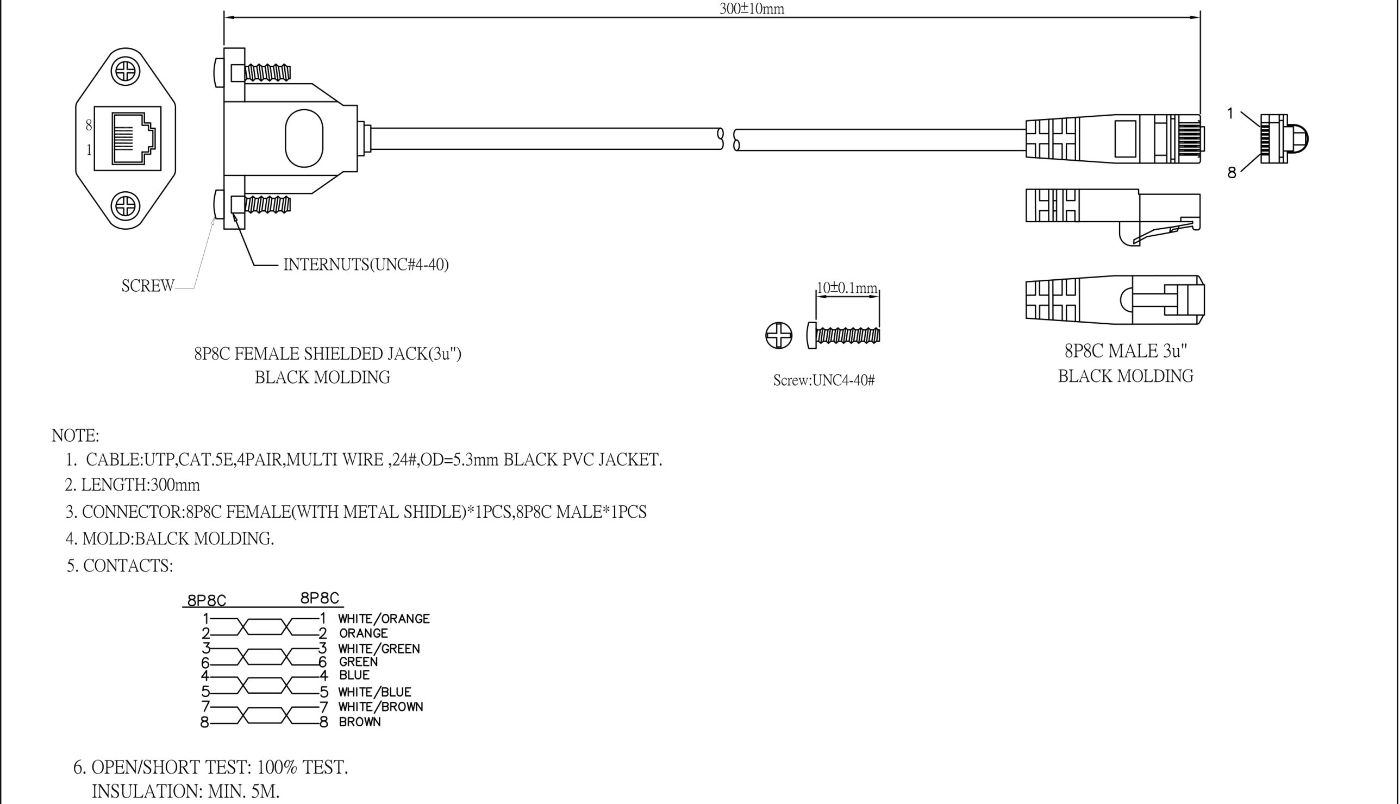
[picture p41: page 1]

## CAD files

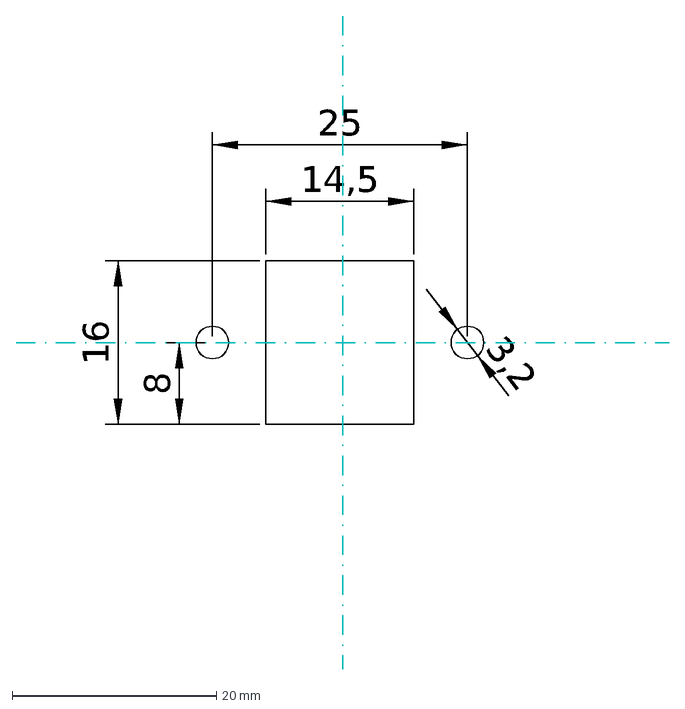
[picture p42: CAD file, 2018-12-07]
hardware/panels/ethernet panel Adafruit 909/ethernet_panel_Adafruit_909.dxf
25
14,5
3,2
8
16

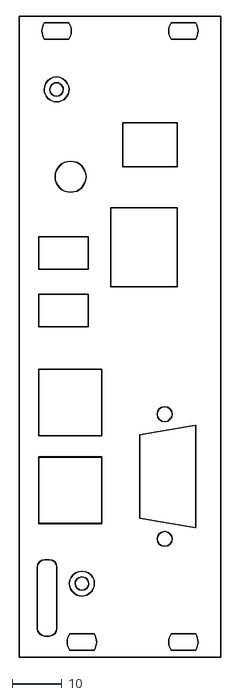
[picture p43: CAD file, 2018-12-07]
hardware/panels/painel para SERIALxxCON.dxf
40.3 x 128.4

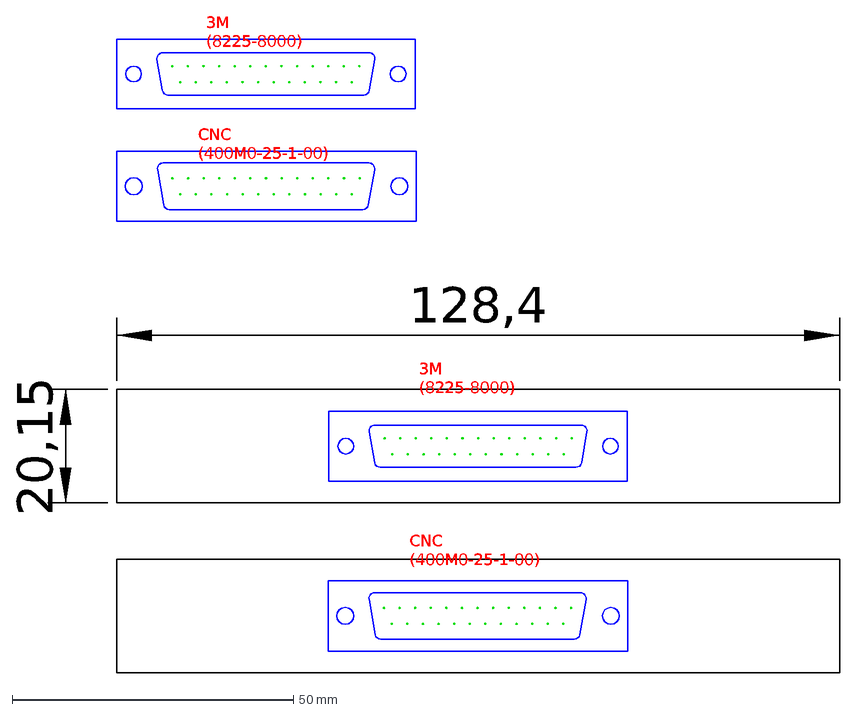
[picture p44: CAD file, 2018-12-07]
hardware/panels/panels for DB25.dxf
3M (8225-8000)
CNC (400M0-25-1-00)
20,15
128,4

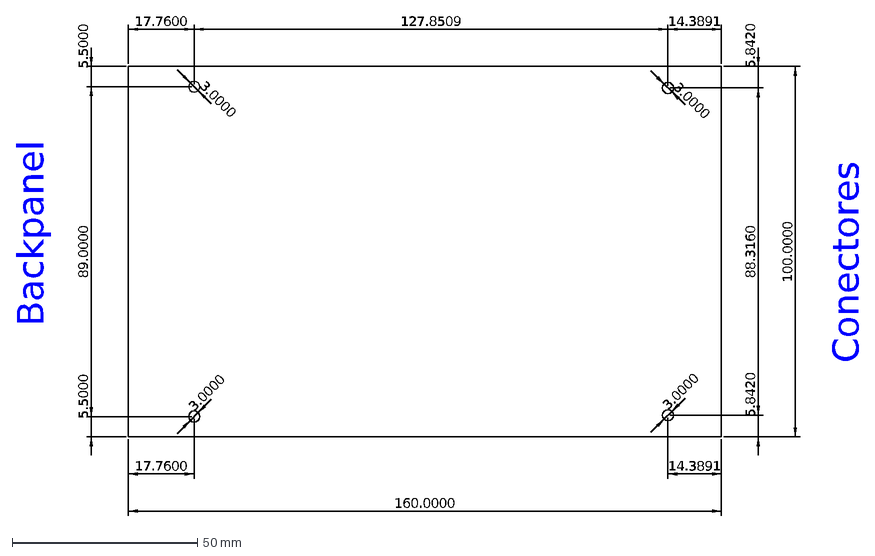
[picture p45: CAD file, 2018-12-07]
hardware/panels/furação para fixação.dxf
17.7600
14.3891
5.5000
5.8420
100.0000
160.0000
88.3160
89.0000
3.0000
127.8509
Conectores
Backpanel

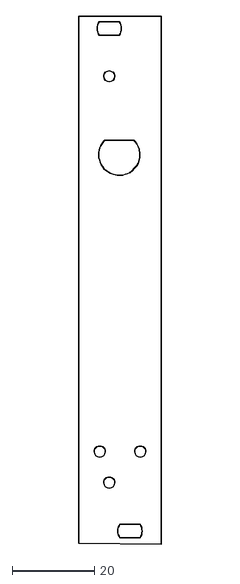
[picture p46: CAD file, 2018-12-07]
hardware/panels/painel para contadora de fotons.dxf
20.1 x 128.6

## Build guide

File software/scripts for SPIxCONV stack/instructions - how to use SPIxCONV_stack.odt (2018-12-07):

Instruções de como utilizar o stack da placa SPIxCONV (conversores DA e AD de 18 bits)

1. Abrir um terminal
2. Fazer acesso SSH na BeagleBone Black:

ssh root@*IP*

  Onde *IP* deve ser substituído pelo endereço IP da BeagleBone Black.
  A senha padrão é “root”.
3. Entrar na pasta “scripts”:

cd /root/scripts

4. Abrir uma shell Python:

python

5. Importar bibliotecas “dac” e “adc”:

import dac

import adc

6. Inicialmente, deve ser feito uma configuração no DAC:

dac.config()

7. Para escrever um valor, devemos usar a função “writeVolts” da biblioteca “dac”:

dac.writeVolts(*value*)

  Onde *value* é um valor entre -10 e 10, sendo sua unidade de medida o Volt.
    Alternativamente, pode ser usada a função “write”, onde, ao invés de um valor em Volts, passamos como parâmetro o código em binário entre 0 e 262143 (2^{18}-1)

dac.write(*value*)

  Onde *value* é um valor entre 0 e 262143.
8. Para ler um valor, devemos usar a função “readVolts” da biblioteca “adc”:

adc.readVolts()

    Alternativamente, pode ser usada a função “read”, onde, ao invés de ler um valor em Volts, será retornado o código em binário entre 0 e 262143 (2^{18}-1)

adc.read()

Controle, julho/2017

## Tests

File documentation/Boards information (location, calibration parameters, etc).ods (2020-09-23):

Board ID | Location | IOC | Pulsed Magnet | Calibration Parameters |  |  |  |  | PV prefix server | Obs.
 |  |  |  | DAC |  | ADC |  | Date of calibration
 |  |  |  | Gain | Offset | Gain | Offset
1 | EPP | ./TB-injection_septum.cmd | Septum de injeção no Booster | 1.00022856796 | -23.604551795 | 1.00031151483 | -25.5034979525 | 14/06/2018 |  | -----
2 | EPP | ./BO-injection_kicker.cmd | Kicker de injeção do Booster | 1.00026576963 | -28.88017967 | 1.00047415222 | -60.215813783 | 14/06/2018 |  | -----
3 | EPP | ./BO-injection_kicker.cmd | Kicker de injeção do Booster | 1.00030796599 | -32.69960318 | 1.000418143 | -47.9227113769 | 18/06/2018 |  | -----
4 | EPP |  |  | 1.00017479634 | -17.242341185 | 1.00026390485 | -31.6174014794 | 19/06/2018 |  | -----
5 | EPP |  |  | 1.00017265115 | -13.97472869 | 1.00045784906 | -39.5533800101 | 19/06/2018 |  | -----
6 | EPP |  |  | 1.00015184443 | -11.674423865 | 1.00060158655 | -59.1729212883 | 19/06/2018 |  | -----
7 | EPP |  |  | 1.00019784934 | -20.91889676 | 1.0002933034 | -24.4439584471 | 19/06/2018 |  | -----
8 | EPP |  |  | 1.00035674834 | -37.7694488 | 1.00029168671 | -34.0324363824 | 19/06/2018 |  | -----
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

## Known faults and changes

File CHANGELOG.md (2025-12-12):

# Changelog

## [0.1.0] - 2025-12-12
First formal public release. 

The project has been running in production for a while, but had no formal versioning until now. This marks the start of the public release history.

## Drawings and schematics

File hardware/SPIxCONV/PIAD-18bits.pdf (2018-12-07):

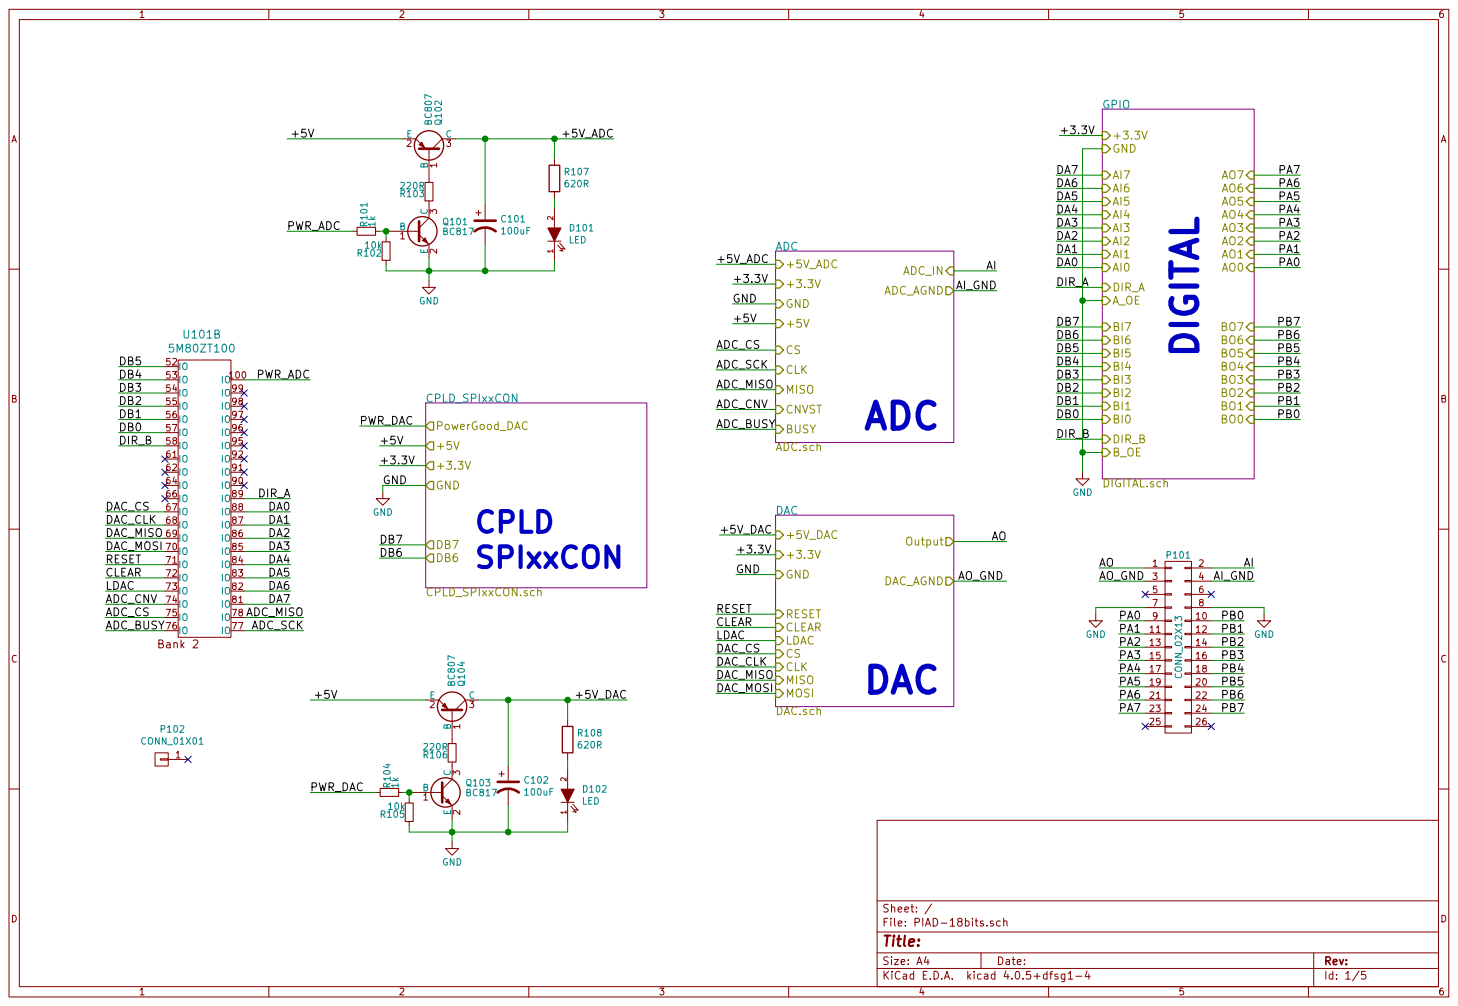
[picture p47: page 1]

Id: 1/5 Title: File: PIAD-18bits.sch Sheet: / CPLD_SPIxxCON

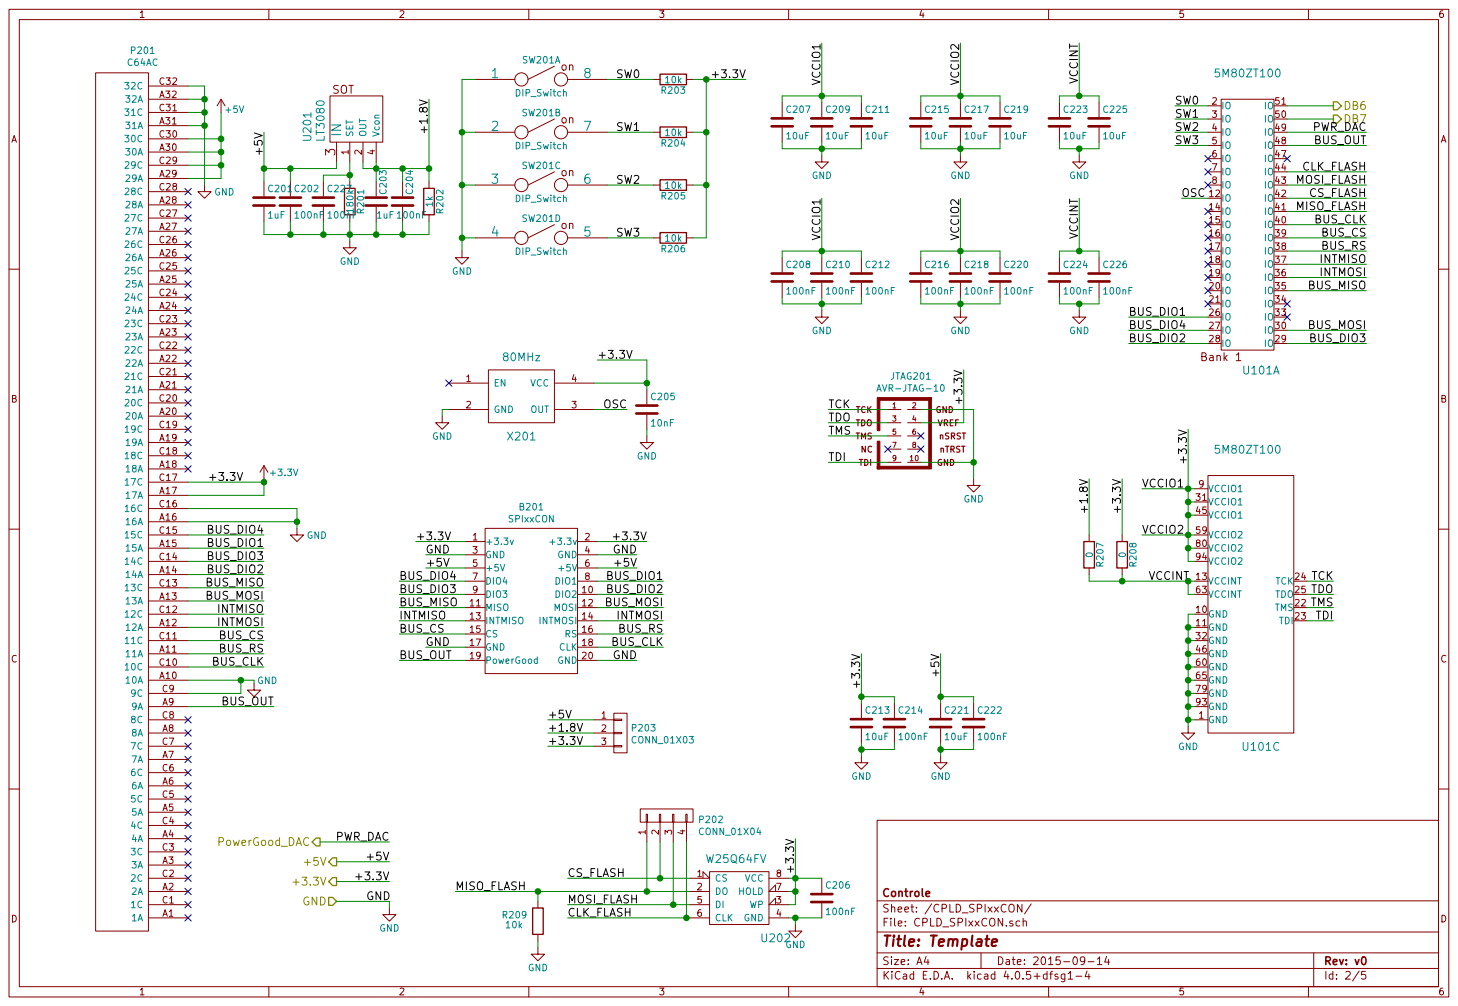
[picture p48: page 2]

IO 14 | MISO_FLASH
IO 15 IO 40

IO 19 | INTMOSI
IO 20 IO 35

INTMISO
INTMOSI

INTMISO | INTMOSI

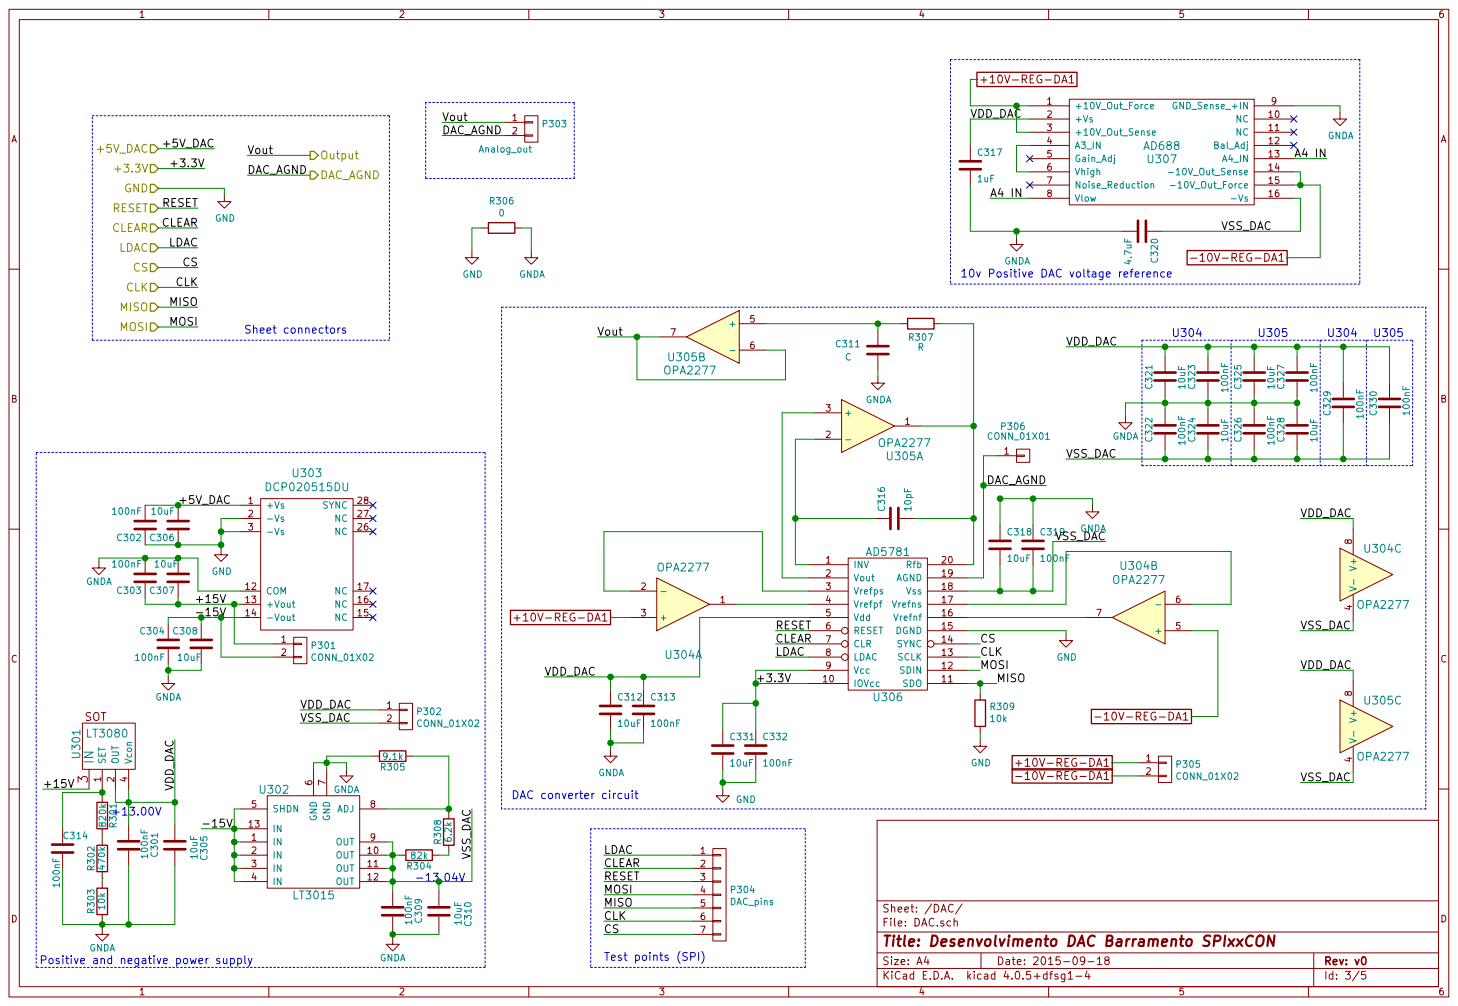
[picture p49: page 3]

10v Positive DAC voltage reference

7 ADJ 8 OUT 9 OUT 10 OUT 11 OUT 12

File: DAC.sch Sheet: /DAC/
Id: 3/5 Title: Desenvolvimento DAC Barramento SPIxxCON

Positive and negative power supply

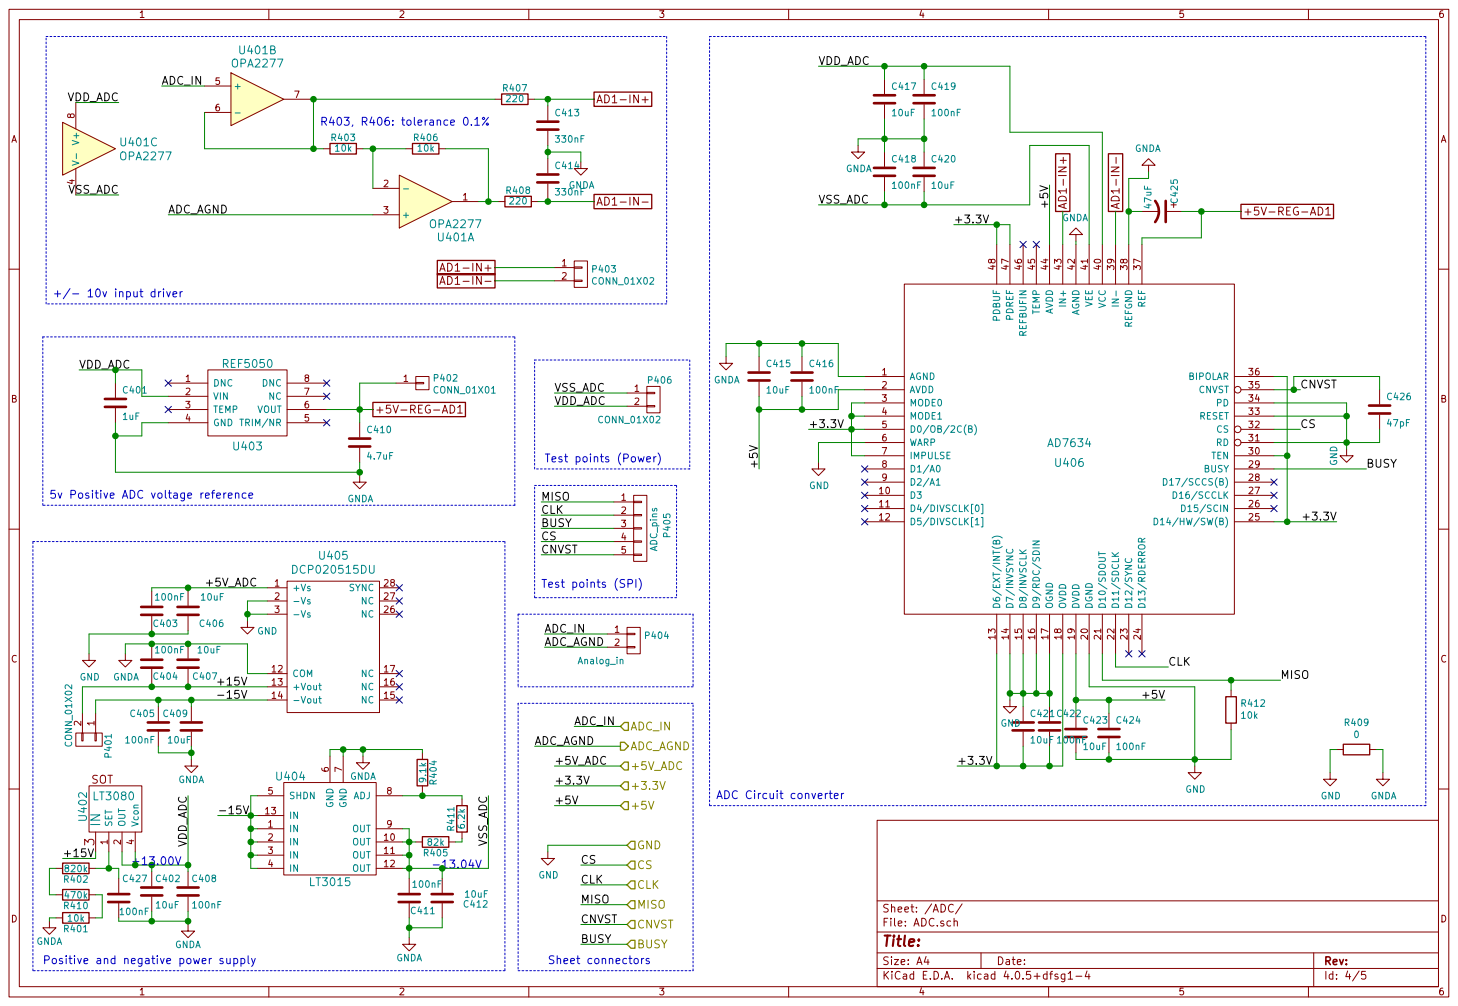
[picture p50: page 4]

VSS_ADC
5v Positive ADC voltage reference R402

100nF Positive and negative power supply

7 ADJ 8 OUT 9 OUT 10 OUT 11 OUT 12

Id: 4/5 Title: File: ADC.sch Sheet: /ADC/

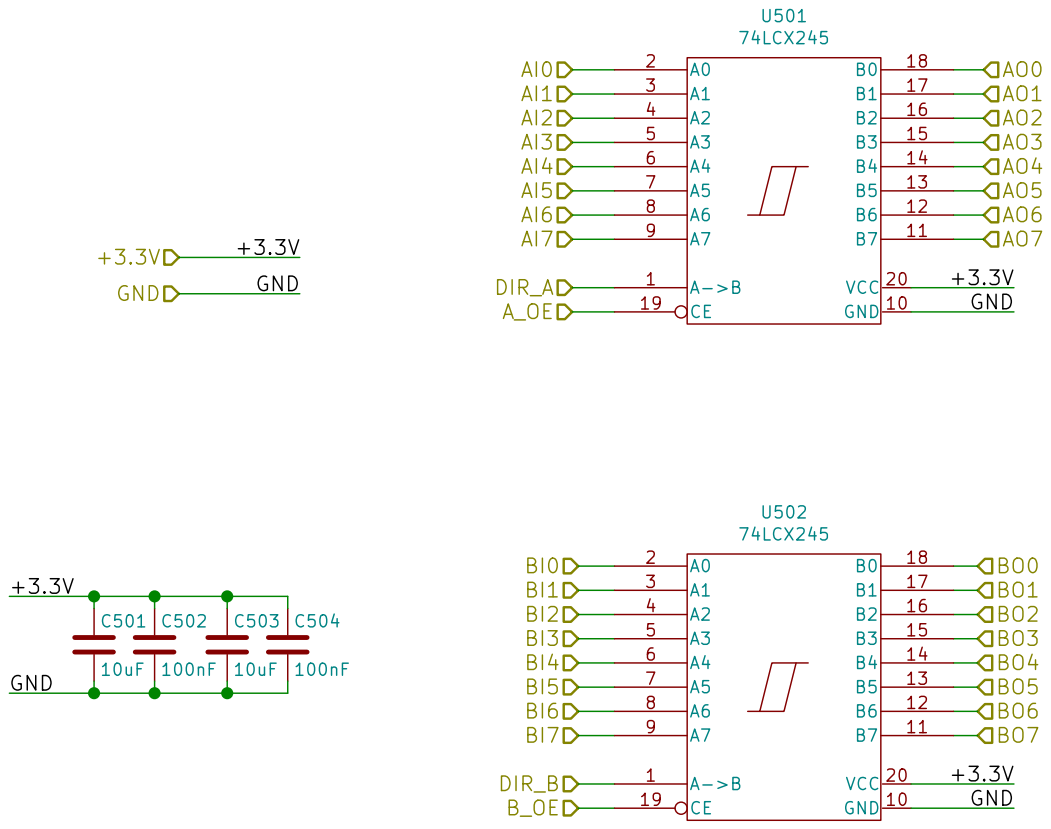
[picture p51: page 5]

Id: 5/5 Title: File: DIGITAL.sch Sheet: /GPIO/

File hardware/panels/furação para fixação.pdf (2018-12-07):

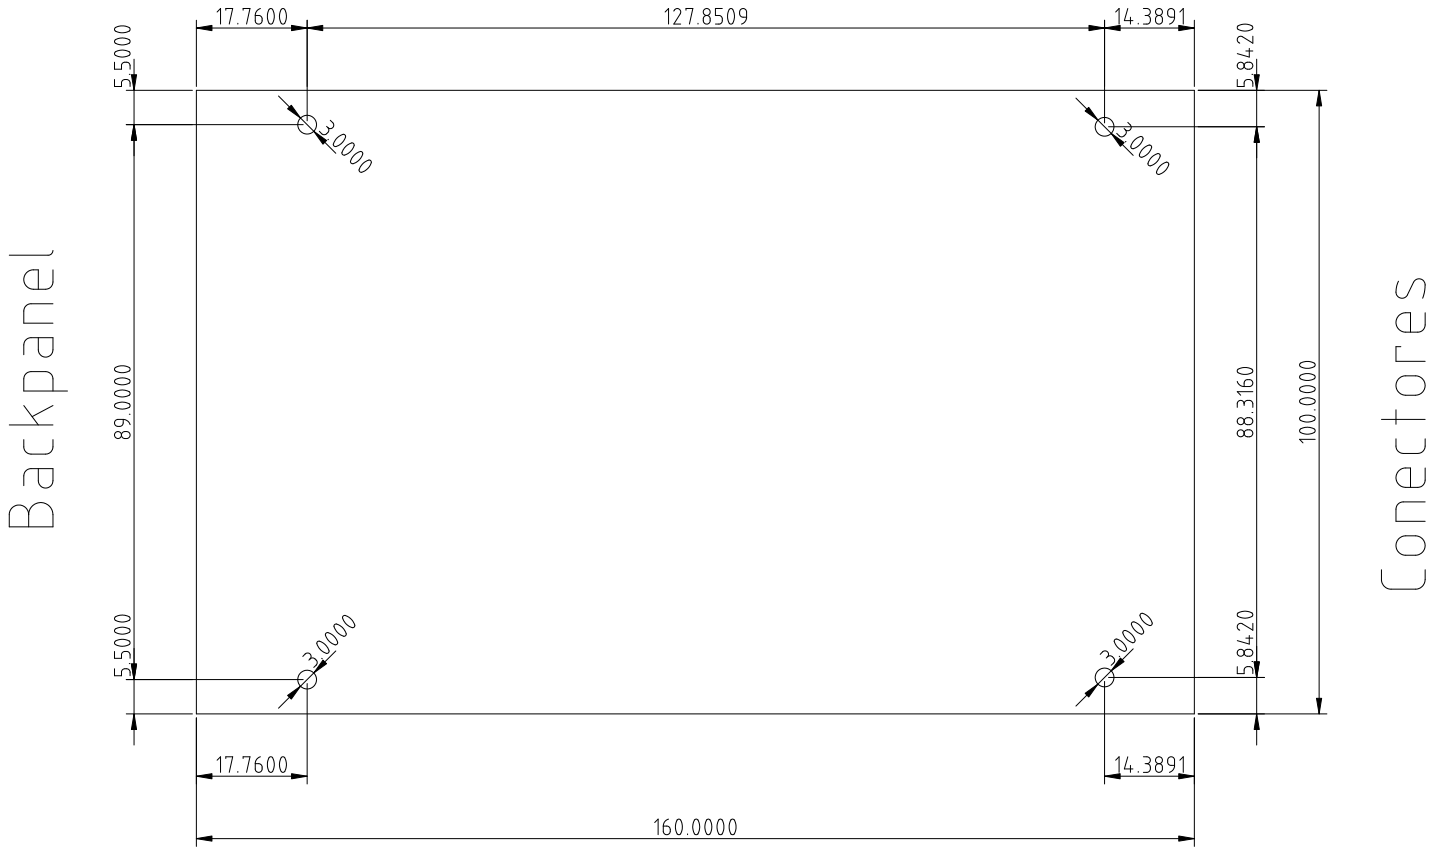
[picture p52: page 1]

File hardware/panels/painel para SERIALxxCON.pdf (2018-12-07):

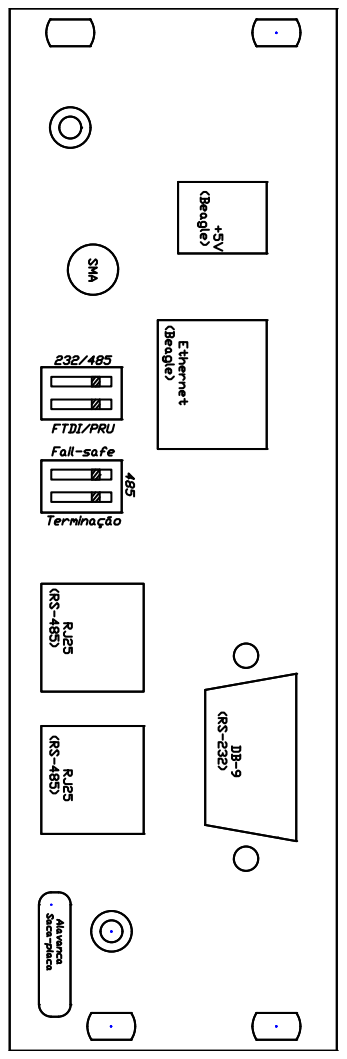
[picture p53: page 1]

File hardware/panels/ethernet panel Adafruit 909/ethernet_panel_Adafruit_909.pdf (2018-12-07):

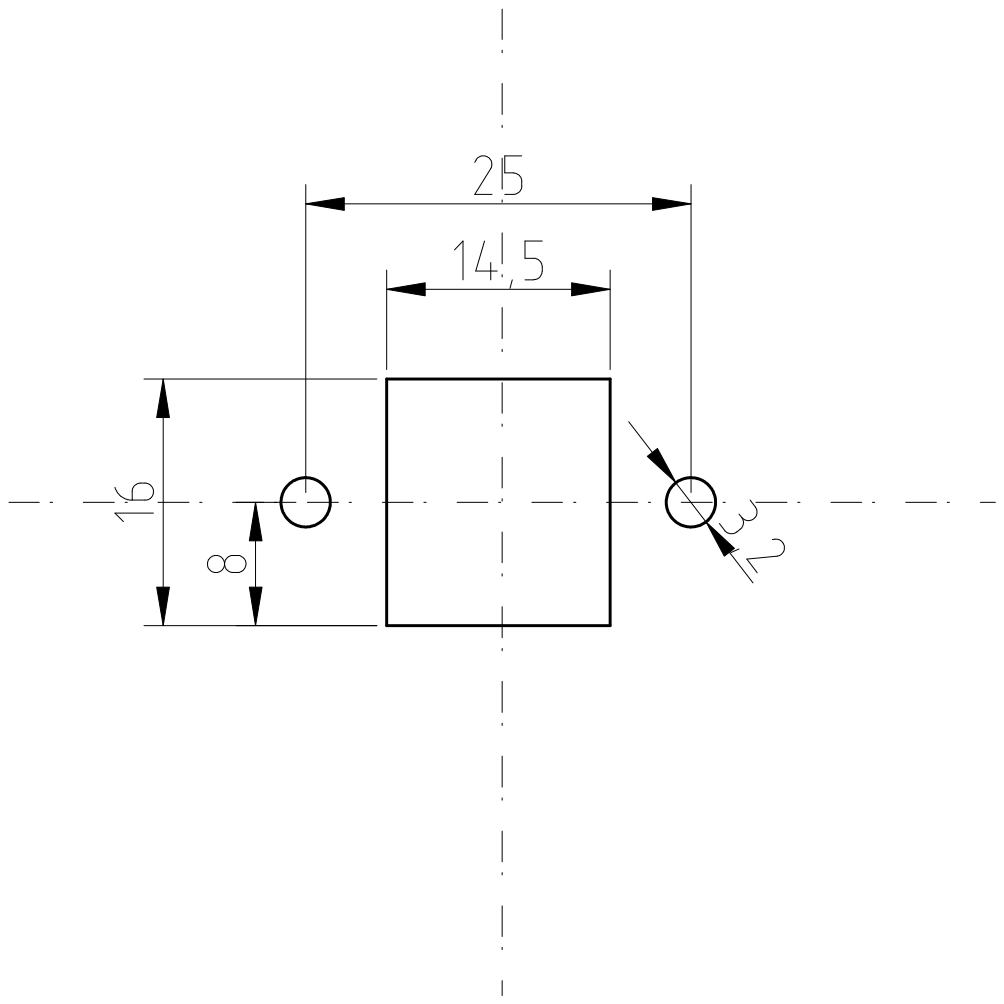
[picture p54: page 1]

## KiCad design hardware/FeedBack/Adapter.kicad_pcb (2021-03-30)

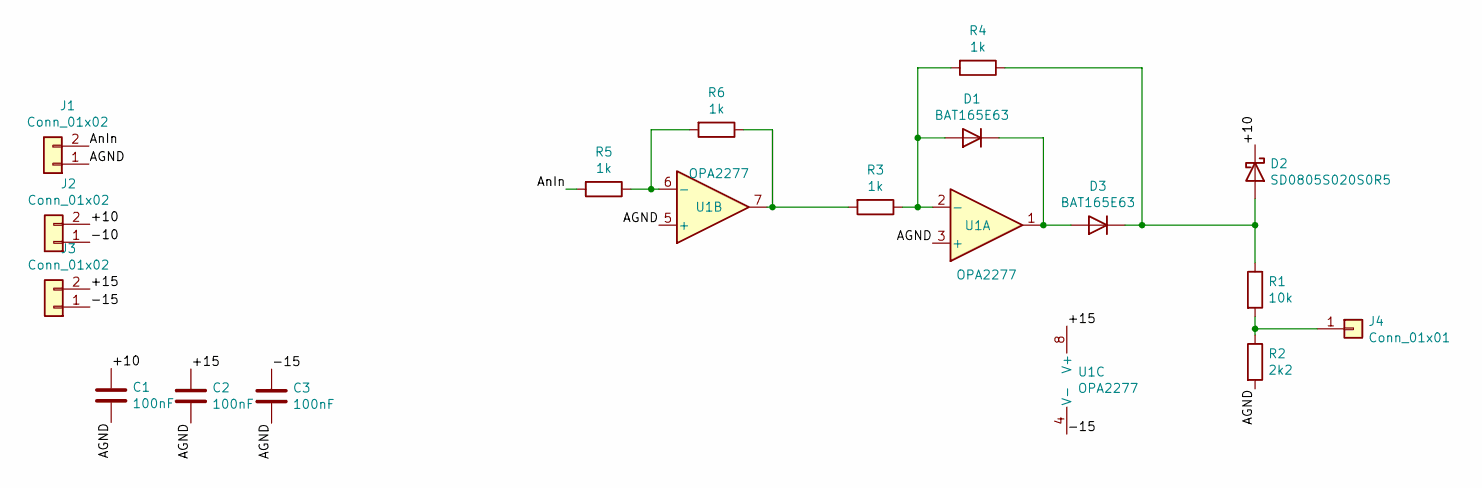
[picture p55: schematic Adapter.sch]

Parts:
C1, C2, C3: 100nF; C_0805_2012Metric_Pad1.18x1.45mm_HandSolder
D1, D3: BAT165E63; D_0805_2012Metric_Pad1.15x1.40mm_HandSolder
D2: SD0805S020S0R5; D_0805_2012Metric_Pad1.15x1.40mm_HandSolder
J1, J2, J3: Conn_01x02; PinSocket_1x02_P2.54mm_Vertical
J4: Conn_01x01; PinSocket_1x01_P2.54mm_Vertical
R1: 10k; R_0805_2012Metric_Pad1.20x1.40mm_HandSolder
R2: 2k2; R_0805_2012Metric_Pad1.20x1.40mm_HandSolder
R3, R4, R5, R6: 1k; R_0805_2012Metric_Pad1.20x1.40mm_HandSolder
U1: OPA2277; SOIC-8_3.9x4.9mm_P1.27mm

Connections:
/+10: C1.1, D2.1 (K), J2.2
/+15: C2.1, J3.2, U1.8 (V+)
/-10: J2.1
/-15: C3.1, J3.1, U1.4 (V-)
/AGND: C1.2, C2.2, C3.2, J1.1, R2.2, U1.3 (+), U1.5 (+)
/AnIn: J1.2, R5.2
unnamed: D1.1 (K), D3.2 (A), U1.1
unnamed: D1.2 (A), R3.1, R4.2, U1.2 (-)
unnamed: D2.2 (A), D3.1 (K), R1.1, R4.1
unnamed: J4.1, R1.2, R2.1
unnamed: R3.2, R6.1, U1.7
unnamed: R5.1, R6.2, U1.6 (-)

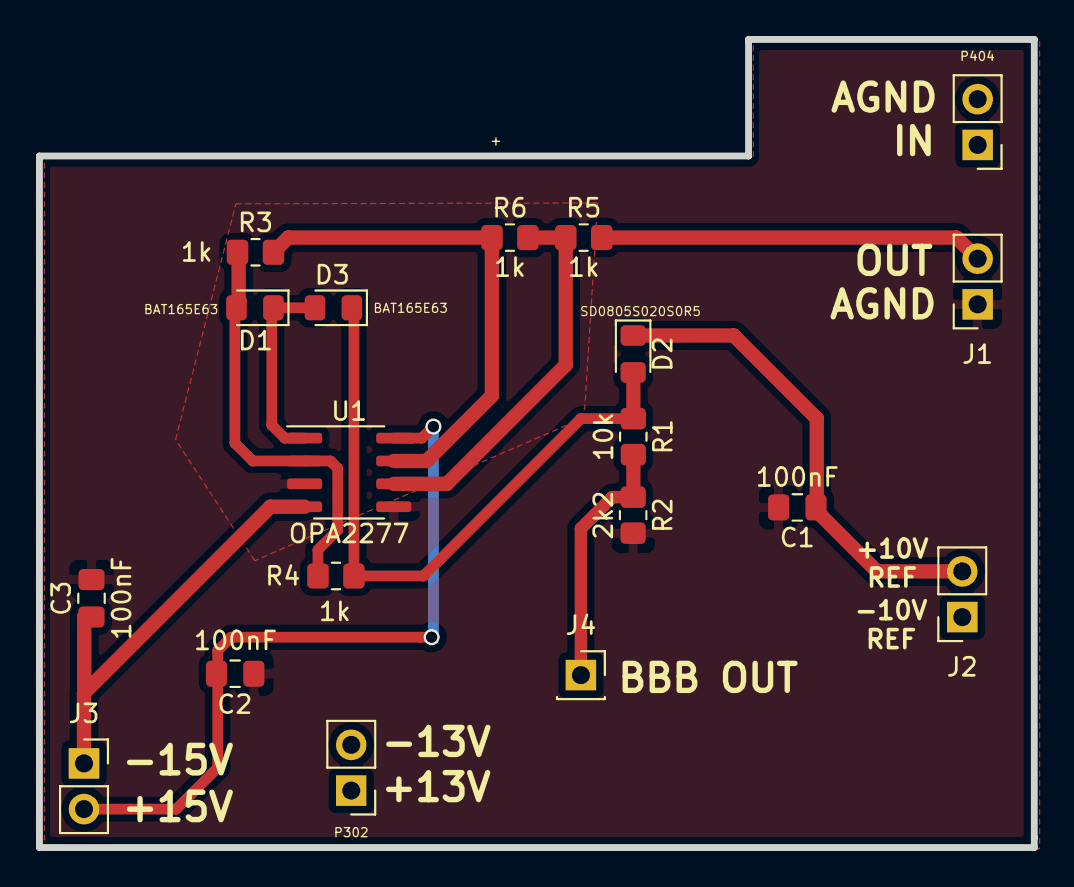
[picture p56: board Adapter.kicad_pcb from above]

Board: 2 copper layers, 55.3 x 44.9 mm, 19 parts (0 on the bottom side), 11 nets.

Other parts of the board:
P302: CONN_01X02; Pin_Header_Straight_1x02_Pitch2.54mm
P404: Analog_in; Pin_Header_Straight_1x02_Pitch2.54mm

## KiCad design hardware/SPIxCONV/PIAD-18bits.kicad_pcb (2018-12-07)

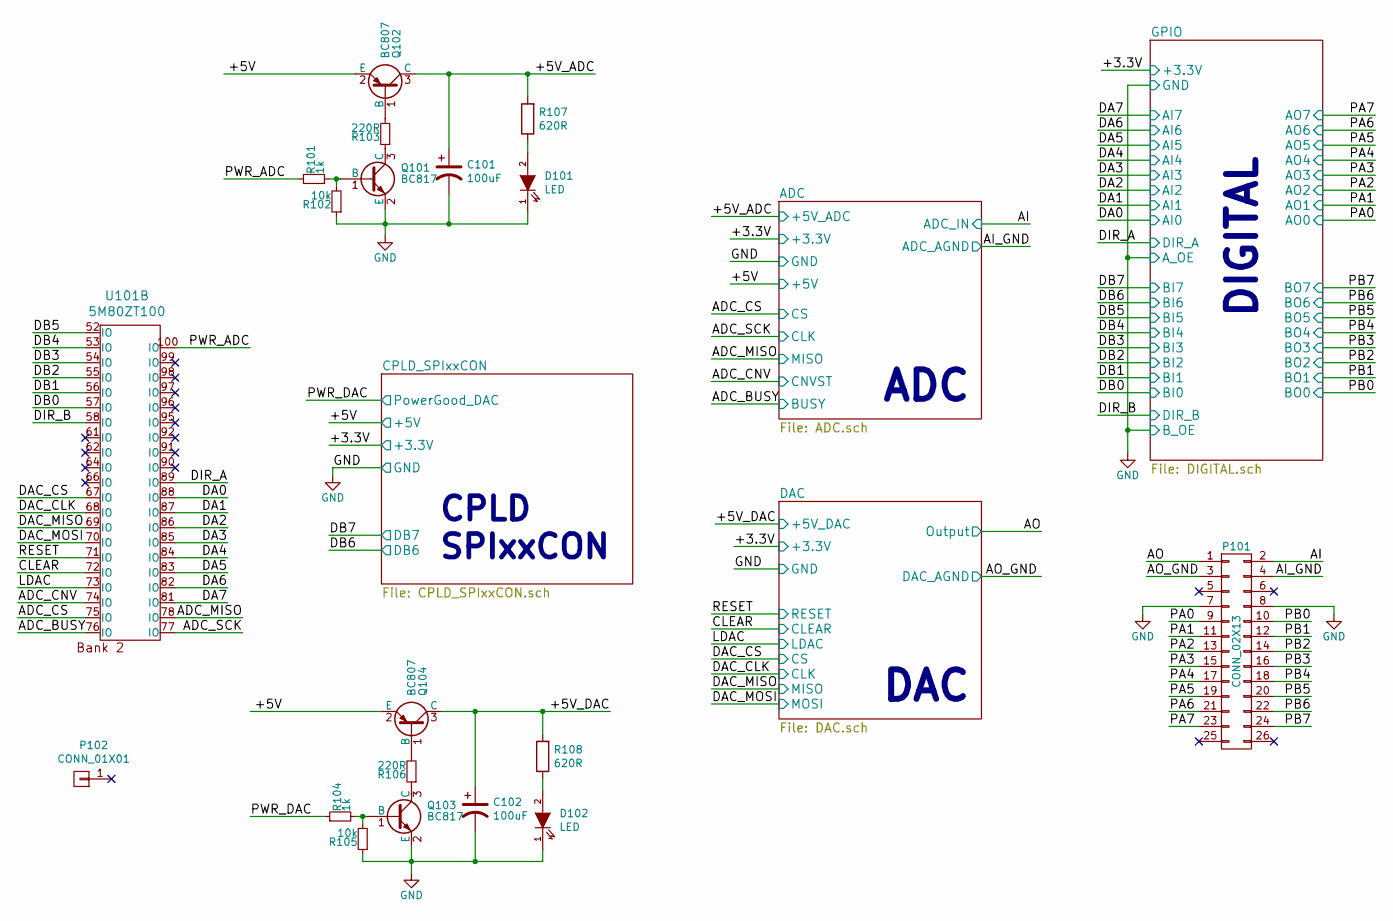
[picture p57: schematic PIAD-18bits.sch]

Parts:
C101, C102: 100uF; CP_Elec_6.3x5.3
D101, D102: LED; LED_0805
P101: CONN_02X13; Pin_Header_Straight_2x13_Pitch2.54mm
P102: CONN_01X01; LNLS_LOGO_Silk
Q101, Q103: BC817; SOT-23
Q102, Q104: BC807; SOT-23
R101, R104: 1k; R_0805
R102, R105: 10k; R_0805
R103, R106: 220R; R_0805
R107, R108: 620R; R_0805
U101: 5M80ZT100; TQFP-100_14x14mm_Pitch0.5mm

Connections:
+5V: Q102.2 (E), Q104.2 (E); also elsewhere on the board
/+5V_ADC: C101.1, Q102.3 (C), R107.2; also elsewhere on the board
/+5V_DAC: C102.1, Q104.3 (C), R108.2; also elsewhere on the board
/ADC_BUSY: U101.76 (IO); also elsewhere on the board
/ADC_CNV: U101.74 (IO); also elsewhere on the board
/ADC_CS: U101.75 (IO); also elsewhere on the board
/ADC_MISO: U101.78 (IO); also elsewhere on the board
/ADC_SCK: U101.77 (IO); also elsewhere on the board
/AI: P101.2; also elsewhere on the board
/AI_GND: P101.4; also elsewhere on the board
/AO: P101.1; also elsewhere on the board
/AO_GND: P101.3; also elsewhere on the board
/CLEAR: U101.72 (IO); also elsewhere on the board
/DA0: U101.88 (IO); also elsewhere on the board
/DA1: U101.87 (IO); also elsewhere on the board
/DA2: U101.86 (IO); also elsewhere on the board
/DA3: U101.85 (IO); also elsewhere on the board
/DA4: U101.84 (IO); also elsewhere on the board
/DA5: U101.83 (IO); also elsewhere on the board
/DA6: U101.82 (IO); also elsewhere on the board
/DA7: U101.81 (IO); also elsewhere on the board
/DAC_CLK: U101.68 (IO); also elsewhere on the board
/DAC_CS: U101.67 (IO); also elsewhere on the board
/DAC_MISO: U101.69 (IO); also elsewhere on the board
/DAC_MOSI: U101.70 (IO); also elsewhere on the board
/DB0: U101.57 (IO); also elsewhere on the board
/DB1: U101.56 (IO); also elsewhere on the board
/DB2: U101.55 (IO); also elsewhere on the board
/DB3: U101.54 (IO); also elsewhere on the board
/DB4: U101.53 (IO); also elsewhere on the board
/DB5: U101.52 (IO); also elsewhere on the board
/DIR_A: U101.89 (IO); also elsewhere on the board
/DIR_B: U101.58 (IO); also elsewhere on the board
/LDAC: U101.73 (IO); also elsewhere on the board
/PA0: P101.9; also elsewhere on the board
/PA1: P101.11; also elsewhere on the board
/PA2: P101.13; also elsewhere on the board
/PA3: P101.15; also elsewhere on the board
/PA4: P101.17; also elsewhere on the board
/PA5: P101.19; also elsewhere on the board
/PA6: P101.21; also elsewhere on the board
/PA7: P101.23; also elsewhere on the board
/PB0: P101.10; also elsewhere on the board
/PB1: P101.12; also elsewhere on the board
/PB2: P101.14; also elsewhere on the board
/PB3: P101.16; also elsewhere on the board
/PB4: P101.18; also elsewhere on the board
/PB5: P101.20; also elsewhere on the board
/PB6: P101.22; also elsewhere on the board
/PB7: P101.24; also elsewhere on the board
/PWR_ADC: R101.1, U101.100 (IO)
/PWR_DAC: R104.1; also elsewhere on the board
/RESET: U101.71 (IO); also elsewhere on the board
GND: C101.2, C102.2, D101.1 (K), D102.1 (K), P101.7, P101.8, Q101.2 (E), Q103.2 (E), R102.1, R105.1; also elsewhere on the board
unnamed: D101.2 (A), R107.1
unnamed: D102.2 (A), R108.1
unnamed: Q101.1 (B), R101.2, R102.2
unnamed: Q101.3 (C), R103.1
unnamed: Q102.1 (B), R103.2
unnamed: Q103.1 (B), R104.2, R105.2
unnamed: Q103.3 (C), R106.1
unnamed: Q104.1 (B), R106.2

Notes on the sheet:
DAC
ADC
DIGITAL
CPLD SPIxxCON

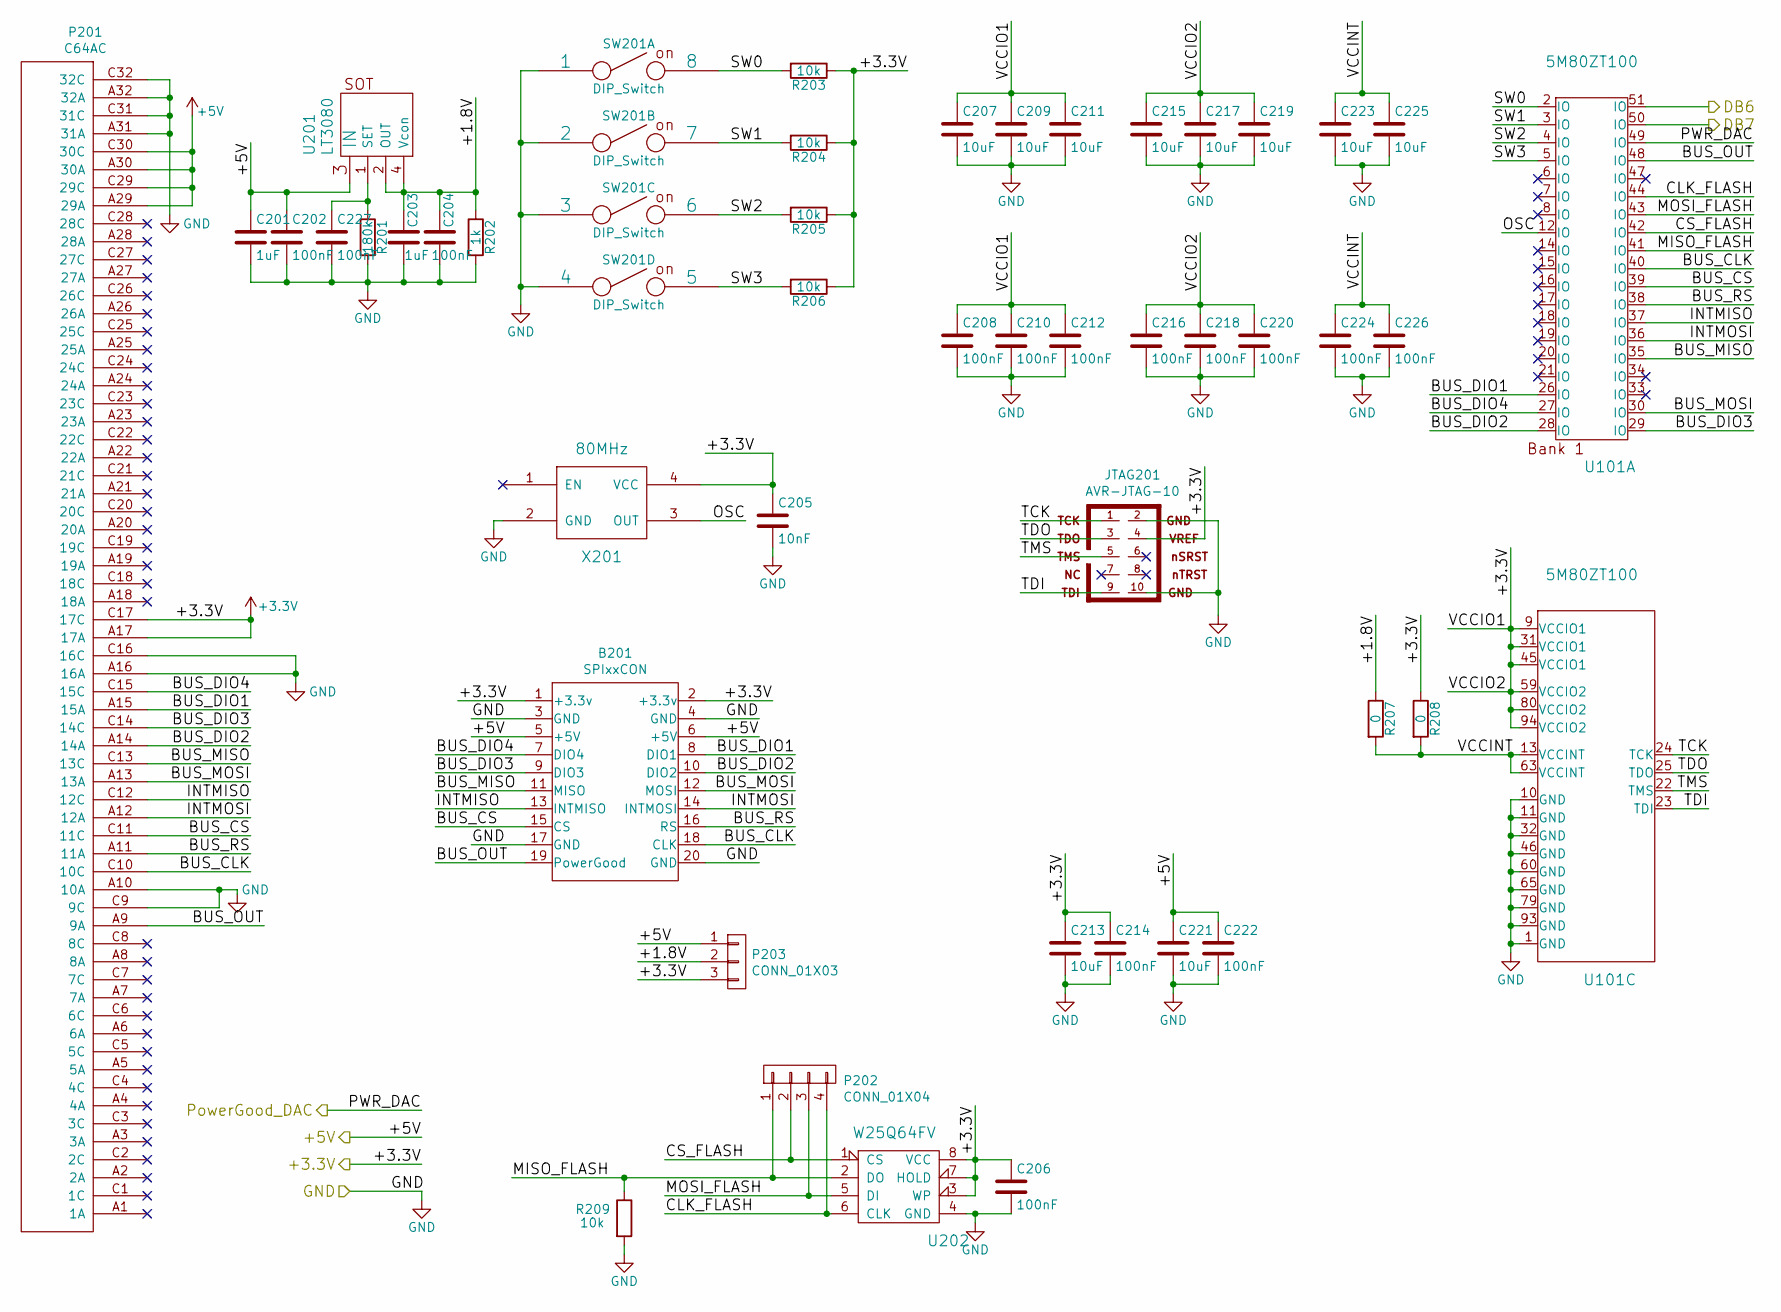
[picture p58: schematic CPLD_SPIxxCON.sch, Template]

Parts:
B201: SPIxxCON; SPIxxCON_(only_connector)
C201, C203: 1uF; C_0805
C202, C204, C206, C208, C210, C212, C214, C216, C218, C220, C222, C224, C226, C227: 100nF; C_0805
C205: 10nF; C_0805
C207, C209, C211, C213, C215, C217, C219, C221, C223, C225: 10uF; C_0805
JTAG201: AVR-JTAG-10; Pin_Header_Straight_2x05_Pitch2.54mm
P201: C64AC; Eurocard_template
P202: CONN_01X04; Pin_Header_Straight_1x04_Pitch2.54mm
P203: CONN_01X03; Pin_Header_Straight_1x03_Pitch2.54mm
R201: 180k; R_0805
R202: 1k; R_0805
R203, R204, R205, R206, R209: 10k; R_0805
R207, R208: 0; R_0805
SW201: DIP_Switch; DIP_switch_SPST_KAE04LGGT
U101: 5M80ZT100; TQFP-100_14x14mm_Pitch0.5mm
U201: LT3080; SOT-223
U202: W25Q64FV; SOIJ-8_5.3x5.3mm_Pitch1.27mm
X201: 80MHz; Oscilador_3.3V_HCMOS_TTL_SMD

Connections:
+3V3: B201.1 (+3.3v), B201.2 (+3.3v), C205.1, C206.1, C207.1, C208.1, C209.1, C210.1, C211.1, C212.1, C213.1, C214.1, C215.1, C216.1, C217.1, C218.1, C219.1, C220.1, JTAG201.4, P201.A17 (17A), P201.C17 (17C), P203.3, R203.1, R204.1, R205.1, R206.1, R208.1, U101.9 (VCCIO1), U101.31 (VCCIO1), U101.45 (VCCIO1), U101.59 (VCCIO2), U101.80 (VCCIO2), U101.94 (VCCIO2), U202.3 (WP), U202.7 (HOLD), U202.8 (VCC), X201.4 (VCC); also elsewhere on the board
+5V: B201.5 (+5V), B201.6 (+5V), C201.1, C202.1, C221.1, C222.1, P201.A29 (29A), P201.A30 (30A), P201.C29 (29C), P201.C30 (30C), P203.1, U201.3 (IN); also elsewhere on the board
/CPLD_SPIxxCON/+1.8V: C203.1, C204.1, P203.2, R202.1, R207.1, U201.2 (OUT), U201.4 (Vcon)
/CPLD_SPIxxCON/BUS_CLK: B201.18 (CLK), P201.C10 (10C), U101.40 (IO)
/CPLD_SPIxxCON/BUS_CS: B201.15 (CS), P201.C11 (11C), U101.39 (IO)
/CPLD_SPIxxCON/BUS_DIO1: B201.8 (DIO1), P201.A15 (15A), U101.26 (IO)
/CPLD_SPIxxCON/BUS_DIO2: B201.10 (DIO2), P201.A14 (14A), U101.28 (IO)
/CPLD_SPIxxCON/BUS_DIO3: B201.9 (DIO3), P201.C14 (14C), U101.29 (IO)
/CPLD_SPIxxCON/BUS_DIO4: B201.7 (DIO4), P201.C15 (15C), U101.27 (IO)
/CPLD_SPIxxCON/BUS_MISO: B201.11 (MISO), P201.C13 (13C), U101.35 (IO)
/CPLD_SPIxxCON/BUS_MOSI: B201.12 (MOSI), P201.A13 (13A), U101.30 (IO)
/CPLD_SPIxxCON/BUS_OUT: B201.19 (PowerGood), P201.A9 (9A), U101.48 (IO)
/CPLD_SPIxxCON/BUS_RS: B201.16 (RS), P201.A11 (11A), U101.38 (IO)
/CPLD_SPIxxCON/CLK_FLASH: P202.4, U101.44 (IO), U202.6 (CLK)
/CPLD_SPIxxCON/CS_FLASH: P202.2, U101.42 (IO), U202.1 (CS)
/CPLD_SPIxxCON/INTMISO: B201.13 (INTMISO), P201.C12 (12C), U101.37 (IO)
/CPLD_SPIxxCON/INTMOSI: B201.14 (INTMOSI), P201.A12 (12A), U101.36 (IO)
/CPLD_SPIxxCON/MISO_FLASH: P202.1, R209.1, U101.41 (IO), U202.2 (DO)
/CPLD_SPIxxCON/MOSI_FLASH: P202.3, U101.43 (IO), U202.5 (DI)
/CPLD_SPIxxCON/OSC: U101.12 (IO), X201.3 (OUT)
/CPLD_SPIxxCON/SW0: R203.2, SW201.8, U101.2 (IO)
/CPLD_SPIxxCON/SW1: R204.2, SW201.7, U101.3 (IO)
/CPLD_SPIxxCON/SW2: R205.2, SW201.6, U101.4 (IO)
/CPLD_SPIxxCON/SW3: R206.2, SW201.5, U101.5 (IO)
/CPLD_SPIxxCON/TCK: JTAG201.1, U101.24 (TCK)
/CPLD_SPIxxCON/TDI: JTAG201.9, U101.23 (TDI)
/CPLD_SPIxxCON/TDO: JTAG201.3, U101.25 (TDO)
/CPLD_SPIxxCON/TMS: JTAG201.5, U101.22 (TMS)
/CPLD_SPIxxCON/VCCINT: C223.1, C224.1, C225.1, C226.1, R207.2, R208.2, U101.13 (VCCINT), U101.63 (VCCINT)
/DB6: U101.51 (IO); also elsewhere on the board
/DB7: U101.50 (IO); also elsewhere on the board
/PWR_DAC: U101.49 (IO); also elsewhere on the board
GND: B201.3 (GND), B201.4 (GND), B201.17 (GND), B201.20 (GND), C201.2, C202.2, C203.2, C204.2, C205.2, C206.2, C207.2, C208.2, C209.2, C210.2, C211.2, C212.2, C213.2, C214.2, C215.2, C216.2, C217.2, C218.2, C219.2, C220.2, C221.2, C222.2, C223.2, C224.2, C225.2, C226.2, C227.2, JTAG201.2, JTAG201.10, P201.A10 (10A), P201.A16 (16A), P201.A31 (31A), P201.A32 (32A), P201.C9 (9C), P201.C16 (16C), P201.C31 (31C), P201.C32 (32C), R201.2, R202.2, R209.2, SW201.1, SW201.2, SW201.3, SW201.4, U101.1 (GND), U101.10 (GND), U101.11 (GND), U101.32 (GND), U101.46 (GND), U101.60 (GND), U101.65 (GND), U101.79 (GND), U101.93 (GND), U202.4 (GND), X201.2 (GND); also elsewhere on the board
unnamed: C227.1, R201.1, U201.1 (SET)

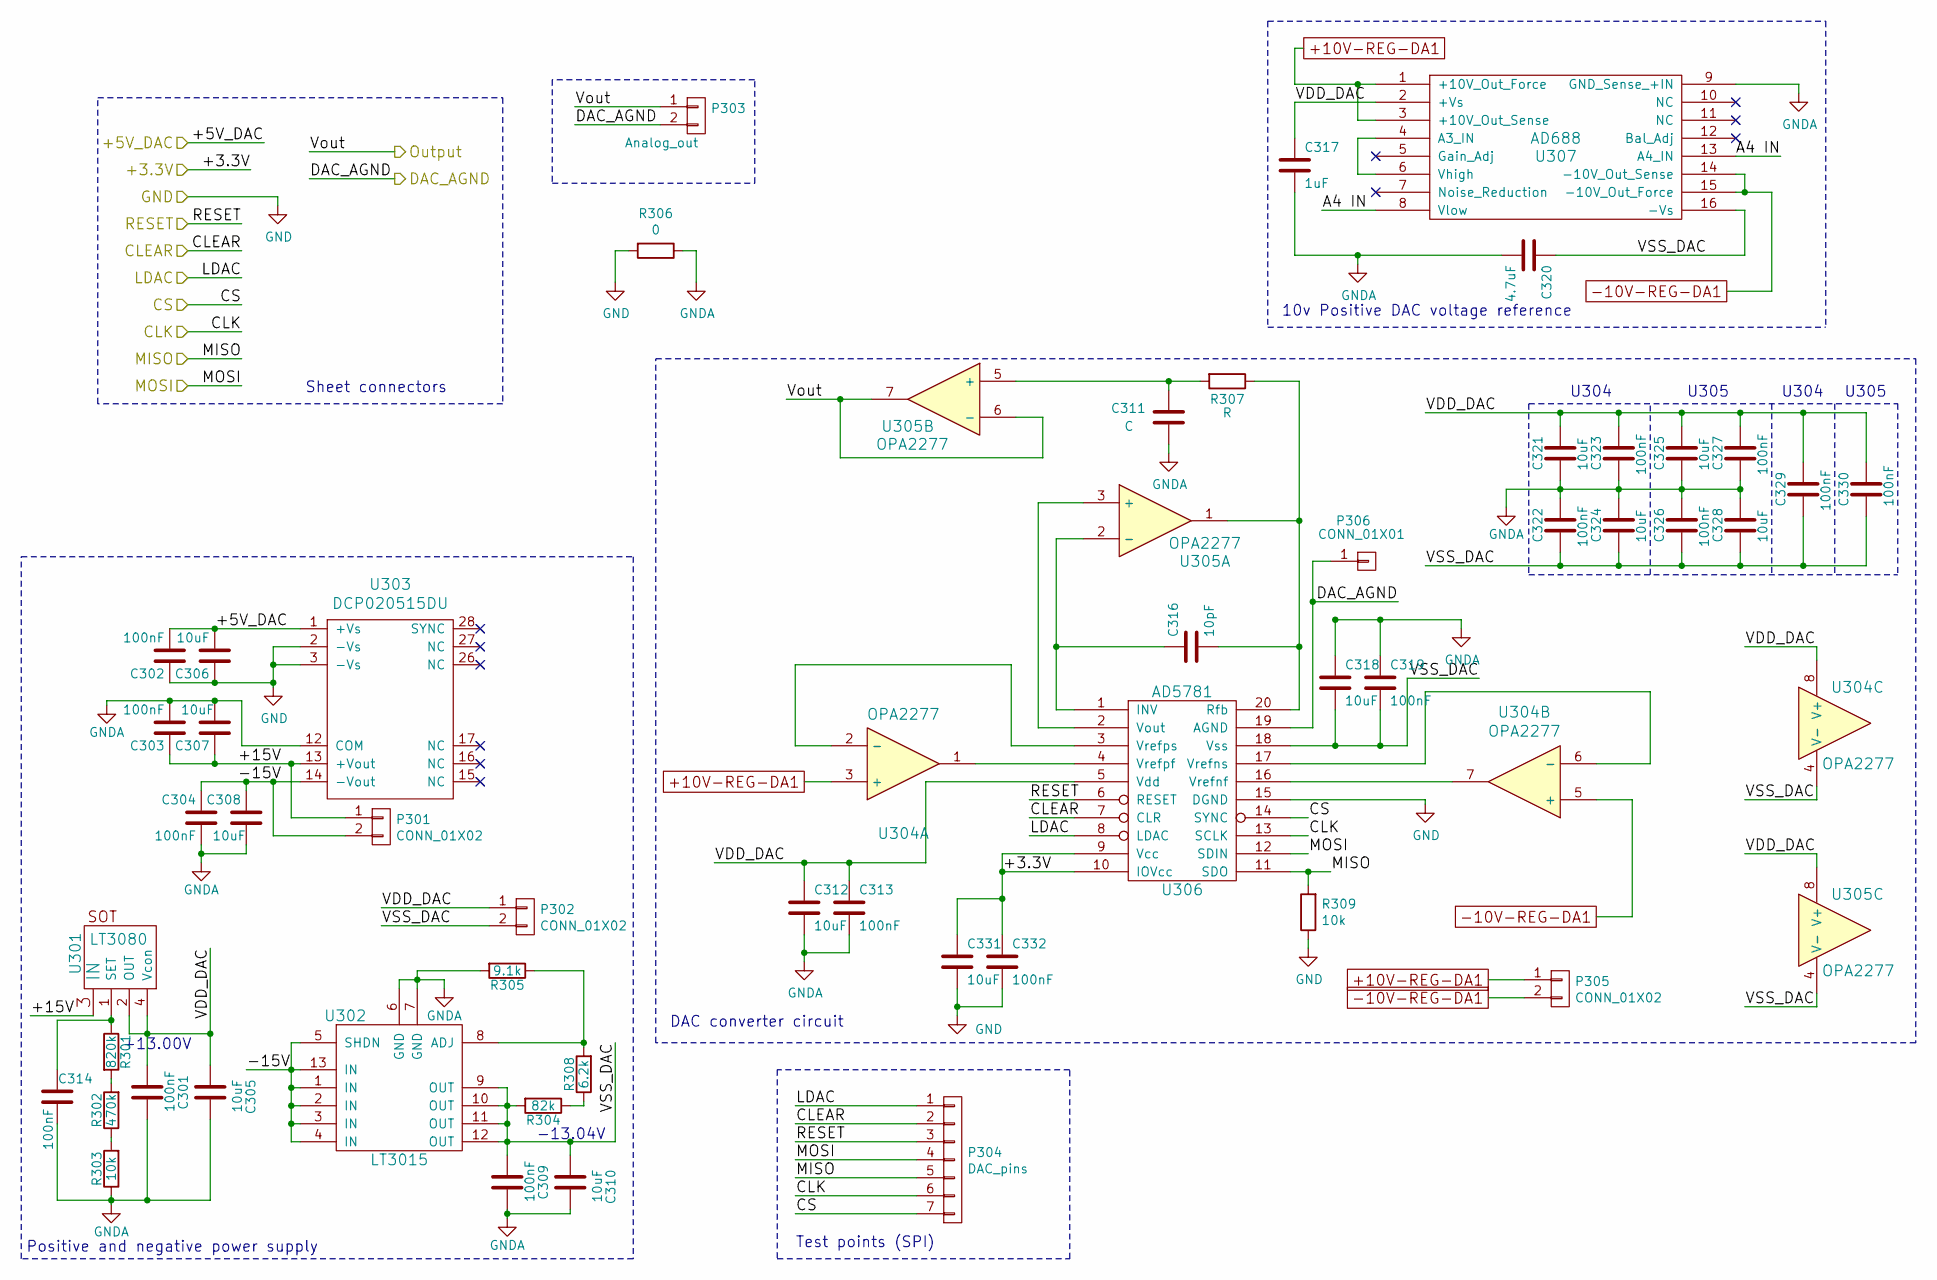
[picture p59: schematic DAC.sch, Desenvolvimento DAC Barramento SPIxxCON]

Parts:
C301, C302, C309, C313, C314, C319, C322, C323, C326, C327, C329, C330, C332: 100nF; C_0805
C303, C304: 100nF; C_0603
C305, C306, C310, C312, C318, C321, C324, C325, C328, C331: 10uF; C_0805
C307, C308: 10uF; CP_Elec_6.3x5.3
C311: C; C_0805
C316: 10pF; C_0805
C317: 1uF; C_0805
C320: 4.7uF; C_1210
P301, P302, P305: CONN_01X02; Pin_Header_Straight_1x02_Pitch2.54mm
P303: Analog_out; Pin_Header_Straight_1x02_Pitch2.54mm
P304: DAC_pins; Pin_Header_Straight_1x07_Pitch2.54mm
P306: CONN_01X01; ground_plane_via
R301: 820k; R_0805
R302: 470k; R_0805
R303, R309: 10k; R_0805
R304: 82k; R_0805
R305: 9.1k; R_0805
R306: 0; R_0805
R307: R; R_0805
R308: 6.2k; R_0805
U301: LT3080; SOT-223
U302: LT3015; MSOP-12-1EP_3x4mm_Pitch0.65mm
U303: DCP020515DU; DCR01XXXXU
U304, U305: OPA2277; SOIC-8_3.9x4.9mm_Pitch1.27mm
U306: AD5781; TSSOP-20_4.4x6.5mm_Pitch0.65mm
U307: AD688; AD688_(SO16W)

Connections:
+3V3: C331.1, C332.1, U306.9 (Vcc), U306.10 (IOVcc); also elsewhere on the board
+10V-REG-DA1: P305.1, U304.3 (+), U307.1 (+10V_Out_Force), U307.3 (+10V_Out_Sense)
-10V-REG-DA1: P305.2, U304.5 (+), U307.14 (-10V_Out_Sense), U307.15 (-10V_Out_Force)
/+5V_DAC: C302.2, C306.2, U303.1 (+Vs); also elsewhere on the board
/AO: P303.1, U305.6 (-), U305.7; also elsewhere on the board
/AO_GND: P303.2, P306.1, P306.2, U306.19 (AGND); also elsewhere on the board
/CLEAR: P304.2, U306.7 (CLR); also elsewhere on the board
/DAC/+15V: C303.1, C307.1, P301.1, U301.3 (IN), U303.13 (+Vout)
/DAC/-15V: C304.1, C308.1, P301.2, U302.1 (IN), U302.2 (IN), U302.3 (IN), U302.4 (IN), U302.5 (SHDN), U302.13 (IN), U303.14 (-Vout)
/DAC/A4 IN: U307.8 (Vlow), U307.13 (A4_IN)
/DAC/VDD_DAC: C301.2, C305.2, C312.1, C313.1, C317.1, C321.1, C323.1, C325.1, C327.1, C329.1, C330.1, P302.1, U301.2 (OUT), U301.4 (Vcon), U304.8 (V+), U305.8 (V+), U306.5 (Vdd), U307.2 (+Vs)
/DAC/VSS_DAC: C309.2, C310.2, C318.2, C319.2, C320.1, C322.2, C324.2, C326.2, C328.2, C329.2, C330.2, P302.2, R304.2, U302.9 (OUT), U302.10 (OUT), U302.11 (OUT), U302.12 (OUT), U304.4 (V-), U305.4 (V-), U306.18 (Vss), U307.16 (-Vs)
/DAC_CLK: P304.6, U306.13 (SCLK); also elsewhere on the board
/DAC_CS: P304.7, U306.14 (SYNC); also elsewhere on the board
/DAC_MISO: P304.5, R309.2, U306.11 (SDO); also elsewhere on the board
/DAC_MOSI: P304.4, U306.12 (SDIN); also elsewhere on the board
/LDAC: P304.1, U306.8 (LDAC); also elsewhere on the board
/RESET: P304.3, U306.6 (RESET); also elsewhere on the board
GND: C302.1, C306.1, C331.2, C332.2, R306.2, R309.1, U303.2 (-Vs), U303.3 (-Vs), U306.15 (DGND); also elsewhere on the board
GNDA: C301.1, C303.2, C304.2, C305.1, C307.2, C308.2, C309.1, C310.1, C311.2, C312.2, C313.2, C314.2, C317.2, C318.1, C319.1, C320.2, C321.2, C322.1, C323.2, C324.1, C325.2, C326.1, C327.2, C328.1, R303.1, R305.2, R306.1, U302.6 (GND), U302.7 (GND), U303.12 (COM), U307.9 (GND_Sense_+IN); also elsewhere on the board
unnamed: C311.1, R307.2, U305.5 (+)
unnamed: C314.1, R301.1, U301.1 (SET)
unnamed: C316.1, U305.2 (-), U306.1 (INV)
unnamed: C316.2, R307.1, U305.1, U306.20 (Rfb)
unnamed: R301.2, R302.2
unnamed: R302.1, R303.2
unnamed: R304.1, R308.1
unnamed: R305.1, R308.2, U302.8 (ADJ)
unnamed: U304.1, U306.4 (Vrefpf)
unnamed: U304.2 (-), U306.3 (Vrefps)
unnamed: U304.6 (-), U306.17 (Vrefns)
unnamed: U304.7, U306.16 (Vrefnf)
unnamed: U305.3 (+), U306.2 (Vout)
unnamed: U307.4 (A3_IN), U307.6 (Vhigh)

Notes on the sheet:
DAC converter circuit
10v Positive DAC voltage reference
Positive and negative power supply
+13.00V
-13.04V
Sheet connectors
Test points (SPI)
U304
U305

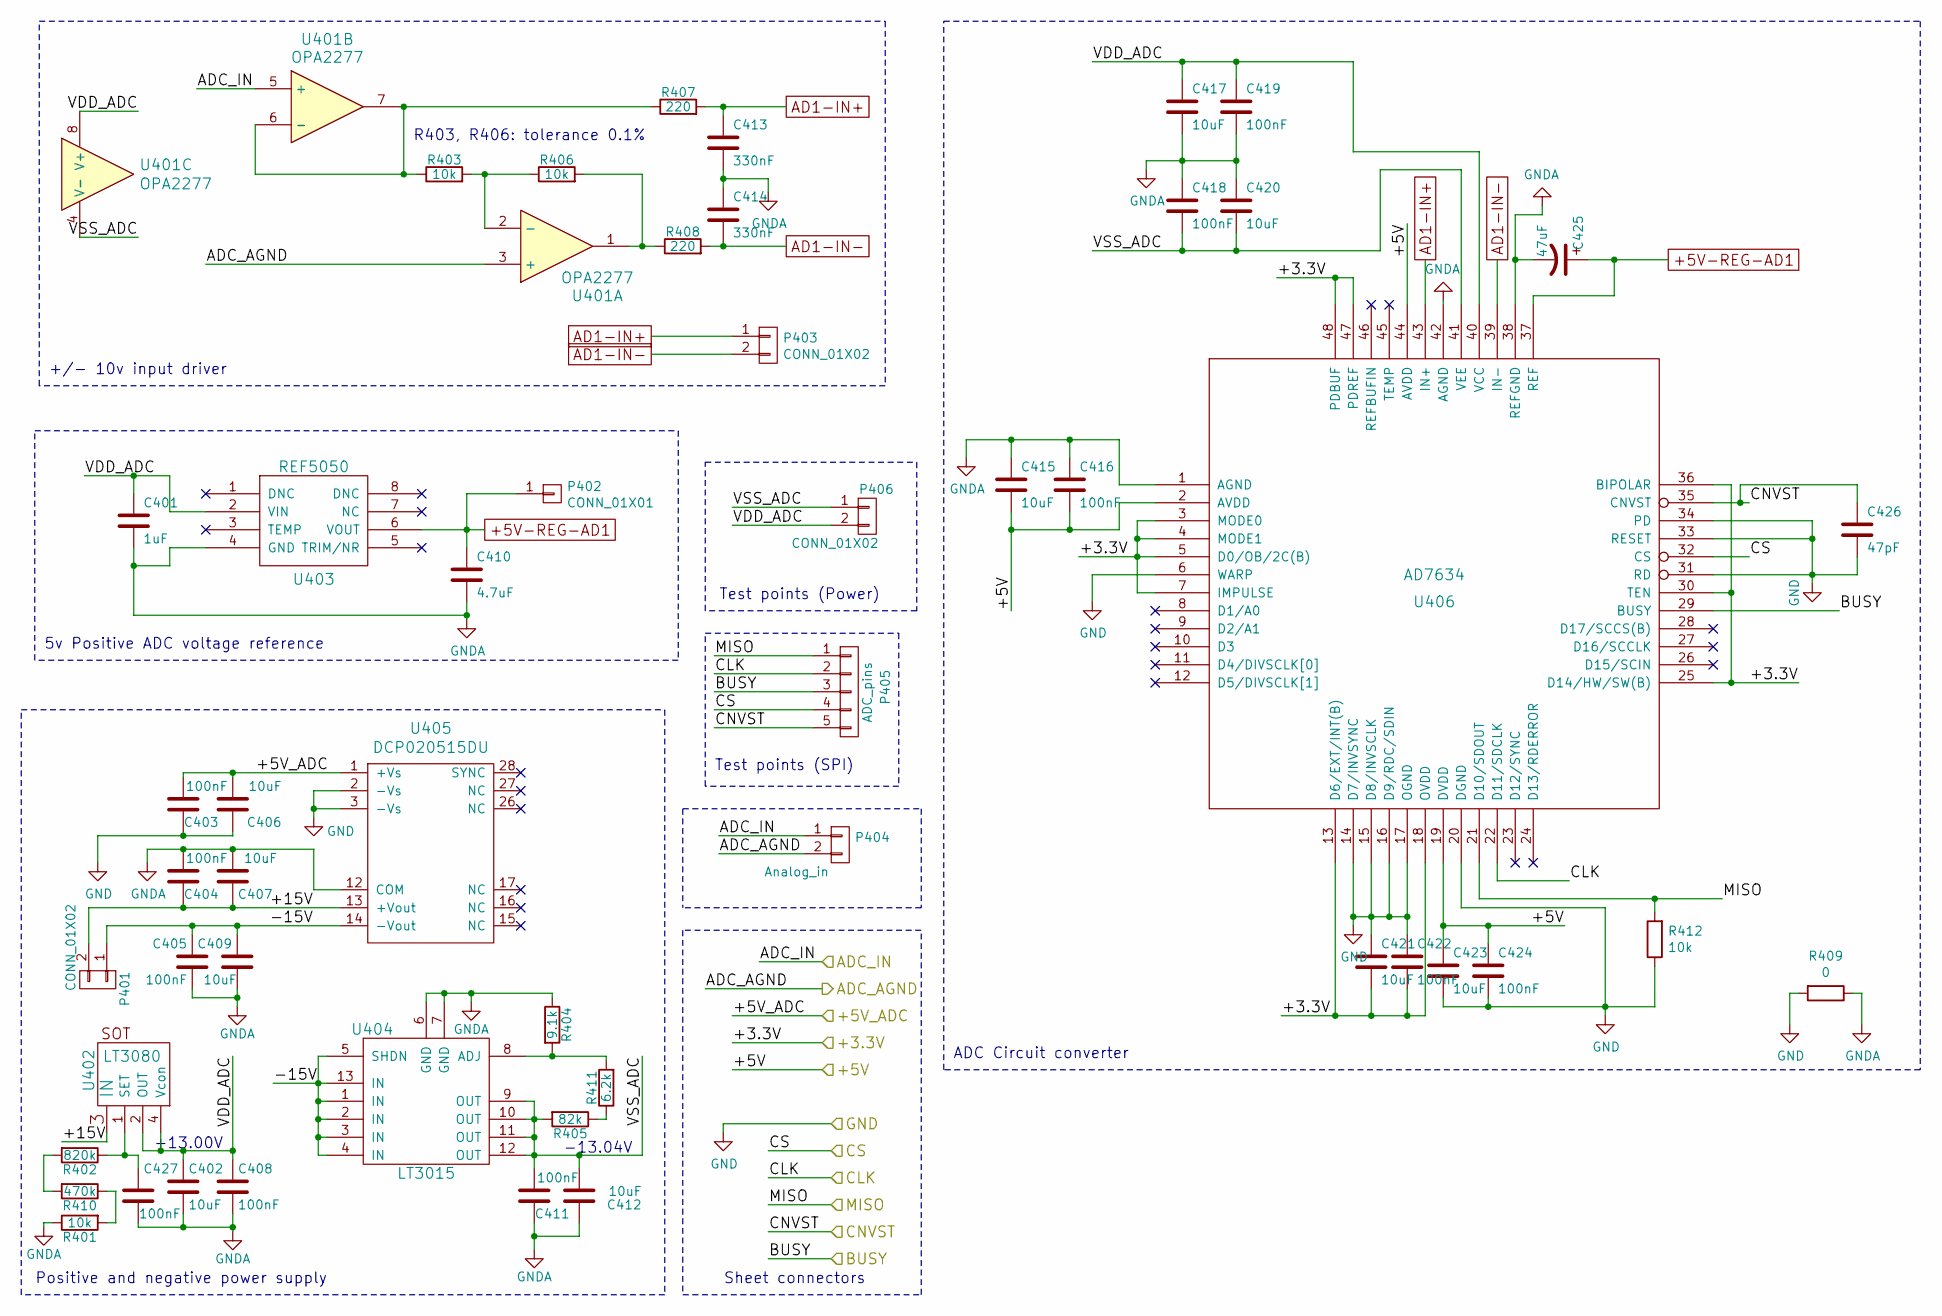
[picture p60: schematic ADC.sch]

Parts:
C401: 1uF; C_0805
C402, C406, C412, C415, C417, C420, C421, C423: 10uF; C_0805
C403, C408, C411, C416, C418, C419, C422, C424, C427: 100nF; C_0805
C404, C405: 100nF; C_0603
C407, C409: 10uF; CP_Elec_6.3x5.3
C410: 4.7uF; C_1210
C413, C414: 330nF; C_0805
C425: 47uF; CP_Elec_6.3x5.3
C426: 47pF; C_0805
P401, P403, P406: CONN_01X02; Pin_Header_Straight_1x02_Pitch2.54mm
P402: CONN_01X01; Pin_Header_Straight_1x01_Pitch2.54mm
P404: Analog_in; Pin_Header_Straight_1x02_Pitch2.54mm
P405: ADC_pins; Pin_Header_Straight_1x05_Pitch2.54mm
R401, R403, R406, R412: 10k; R_0805
R402: 820k; R_0805
R404: 9.1k; R_0805
R405: 82k; R_0805
R407, R408: 220; R_0805
R409: 0; R_0805
R410: 470k; R_0805
R411: 6.2k; R_0805
U401: OPA2277; SOIC-8_3.9x4.9mm_Pitch1.27mm
U402: LT3080; SOT-223
U403: REF5050; SOIC-8_3.9x4.9mm_Pitch1.27mm
U404: LT3015; MSOP-12-1EP_3x4mm_Pitch0.65mm
U405: DCP020515DU; DCR01XXXXU
U406: AD7634; LQFP-48_7x7mm_Pitch0.5mm

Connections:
+3V3: C421.2, C422.2, U406.3 (MODE0), U406.4 (MODE1), U406.5 (D0/OB/2C(B)), U406.7 (IMPULSE), U406.13 (D6/EXT/INT(B)), U406.18 (OVDD), U406.25 (D14/HW/SW(B)), U406.30 (TEN), U406.36 (BIPOLAR), U406.47 (PDREF), U406.48 (PDBUF); also elsewhere on the board
+5V: C415.2, C416.2, C423.1, C424.1, U406.2 (AVDD), U406.19 (DVDD), U406.44 (AVDD); also elsewhere on the board
+5V-REG-AD1: C410.1, C425.1, P402.1, U403.6 (VOUT), U406.37 (REF)
/+5V_ADC: C403.2, C406.2, U405.1 (+Vs); also elsewhere on the board
/ADC/+15V: C404.1, C407.1, P401.2, U402.3 (IN), U405.13 (+Vout)
/ADC/-15V: C405.1, C409.1, P401.1, U404.1 (IN), U404.2 (IN), U404.3 (IN), U404.4 (IN), U404.5 (SHDN), U404.13 (IN), U405.14 (-Vout)
/ADC/VDD_ADC: C401.1, C402.1, C408.1, C417.1, C419.1, P406.2, U401.8 (V+), U402.2 (OUT), U402.4 (Vcon), U403.2 (VIN), U406.40 (VCC)
/ADC/VSS_ADC: C411.2, C412.2, C418.2, C420.2, P406.1, R405.2, U401.4 (V-), U404.9 (OUT), U404.10 (OUT), U404.11 (OUT), U404.12 (OUT), U406.41 (VEE)
/ADC_BUSY: P405.3, U406.29 (BUSY); also elsewhere on the board
/ADC_CNV: C426.1, P405.5, U406.35 (CNVST); also elsewhere on the board
/ADC_CS: P405.4, U406.32 (CS); also elsewhere on the board
/ADC_MISO: P405.1, R412.2, U406.21 (D10/SDOUT); also elsewhere on the board
/ADC_SCK: P405.2, U406.22 (D11/SDCLK); also elsewhere on the board
/AI: P404.1, U401.5 (+); also elsewhere on the board
/AI_GND: P404.2, U401.3 (+); also elsewhere on the board
AD1-IN+: C413.1, P403.1, R407.2, U406.43 (IN+)
AD1-IN-: C414.2, P403.2, R408.2, U406.39 (IN-)
GND: C403.1, C406.1, C421.1, C422.1, C423.2, C424.2, C426.2, R409.2, R412.1, U405.2 (-Vs), U405.3 (-Vs), U406.6 (WARP), U406.14 (D7/INVSYNC), U406.15 (D8/INVSCLK), U406.16 (D9/RDC/SDIN), U406.17 (OGND), U406.20 (DGND), U406.31 (RD), U406.33 (RESET), U406.34 (PD); also elsewhere on the board
GNDA: C401.2, C402.2, C404.2, C405.2, C407.2, C408.2, C409.2, C410.2, C411.1, C412.1, C413.2, C414.1, C415.1, C416.1, C417.2, C418.1, C419.2, C420.1, C425.2, C427.2, R401.1, R404.1, R409.1, U403.4 (GND), U404.6 (GND), U404.7 (GND), U405.12 (COM), U406.1 (AGND), U406.38 (REFGND), U406.42 (AGND); also elsewhere on the board
unnamed: C427.1, R402.1, U402.1 (SET)
unnamed: R401.2, R410.1
unnamed: R402.2, R410.2
unnamed: R403.1, R407.1, U401.6 (-), U401.7
unnamed: R403.2, R406.1, U401.2 (-)
unnamed: R404.2, R411.2, U404.8 (ADJ)
unnamed: R405.1, R411.1
unnamed: R406.2, R408.1, U401.1

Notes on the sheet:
5v Positive ADC voltage reference
Positive and negative power supply
-13.04V
+/- 10v input driver
ADC Circuit converter
Sheet connectors
Test points (SPI)
Test points (Power)
R403, R406: tolerance 0.1%
+13.00V

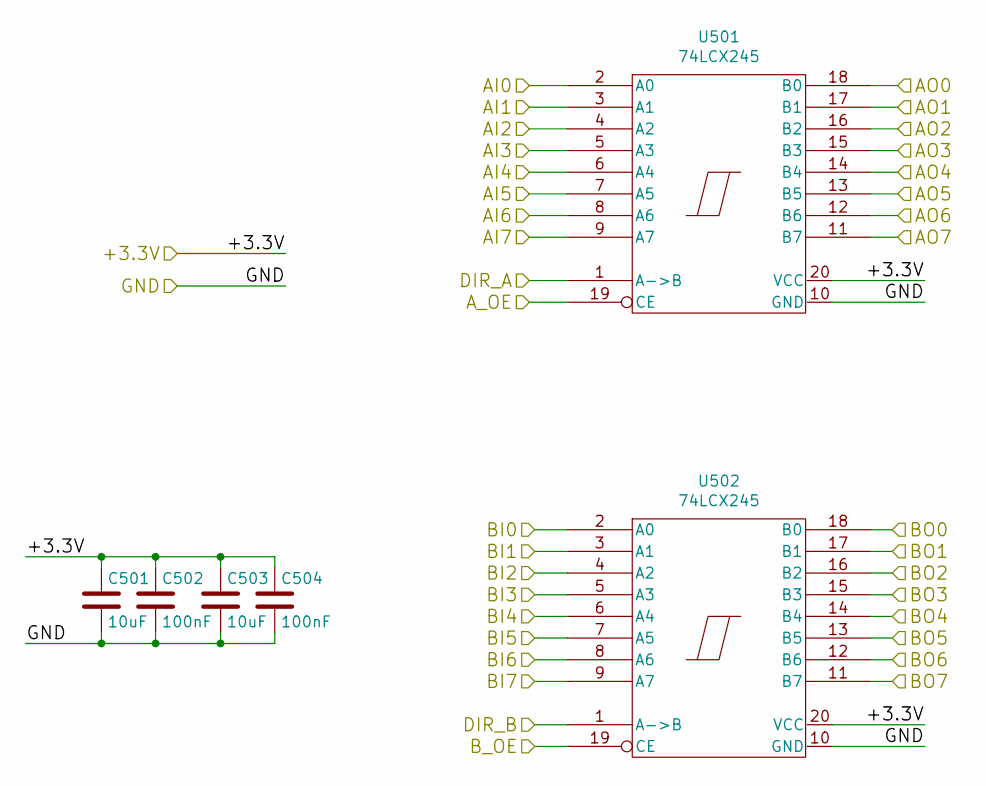
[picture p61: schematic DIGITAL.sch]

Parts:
C501, C503: 10uF; C_0805
C502, C504: 100nF; C_0805
U501, U502: 74LCX245; SOIC-20W_7.5x12.8mm_Pitch1.27mm

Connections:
+3V3: C501.1, C502.1, C503.1, C504.1, U501.20 (VCC), U502.20 (VCC); also elsewhere on the board
/DA0: U501.2 (A0); also elsewhere on the board
/DA1: U501.3 (A1); also elsewhere on the board
/DA2: U501.4 (A2); also elsewhere on the board
/DA3: U501.5 (A3); also elsewhere on the board
/DA4: U501.6 (A4); also elsewhere on the board
/DA5: U501.7 (A5); also elsewhere on the board
/DA6: U501.8 (A6); also elsewhere on the board
/DA7: U501.9 (A7); also elsewhere on the board
/DB0: U502.2 (A0); also elsewhere on the board
/DB1: U502.3 (A1); also elsewhere on the board
/DB2: U502.4 (A2); also elsewhere on the board
/DB3: U502.5 (A3); also elsewhere on the board
/DB4: U502.6 (A4); also elsewhere on the board
/DB5: U502.7 (A5); also elsewhere on the board
/DB6: U502.8 (A6); also elsewhere on the board
/DB7: U502.9 (A7); also elsewhere on the board
/DIR_A: U501.1 (A->B); also elsewhere on the board
/DIR_B: U502.1 (A->B); also elsewhere on the board
/PA0: U501.18 (B0); also elsewhere on the board
/PA1: U501.17 (B1); also elsewhere on the board
/PA2: U501.16 (B2); also elsewhere on the board
/PA3: U501.15 (B3); also elsewhere on the board
/PA4: U501.14 (B4); also elsewhere on the board
/PA5: U501.13 (B5); also elsewhere on the board
/PA6: U501.12 (B6); also elsewhere on the board
/PA7: U501.11 (B7); also elsewhere on the board
/PB0: U502.18 (B0); also elsewhere on the board
/PB1: U502.17 (B1); also elsewhere on the board
/PB2: U502.16 (B2); also elsewhere on the board
/PB3: U502.15 (B3); also elsewhere on the board
/PB4: U502.14 (B4); also elsewhere on the board
/PB5: U502.13 (B5); also elsewhere on the board
/PB6: U502.12 (B6); also elsewhere on the board
/PB7: U502.11 (B7); also elsewhere on the board
GND: C501.2, C502.2, C503.2, C504.2, U501.10 (GND), U501.19 (CE), U502.10 (GND), U502.19 (CE); also elsewhere on the board

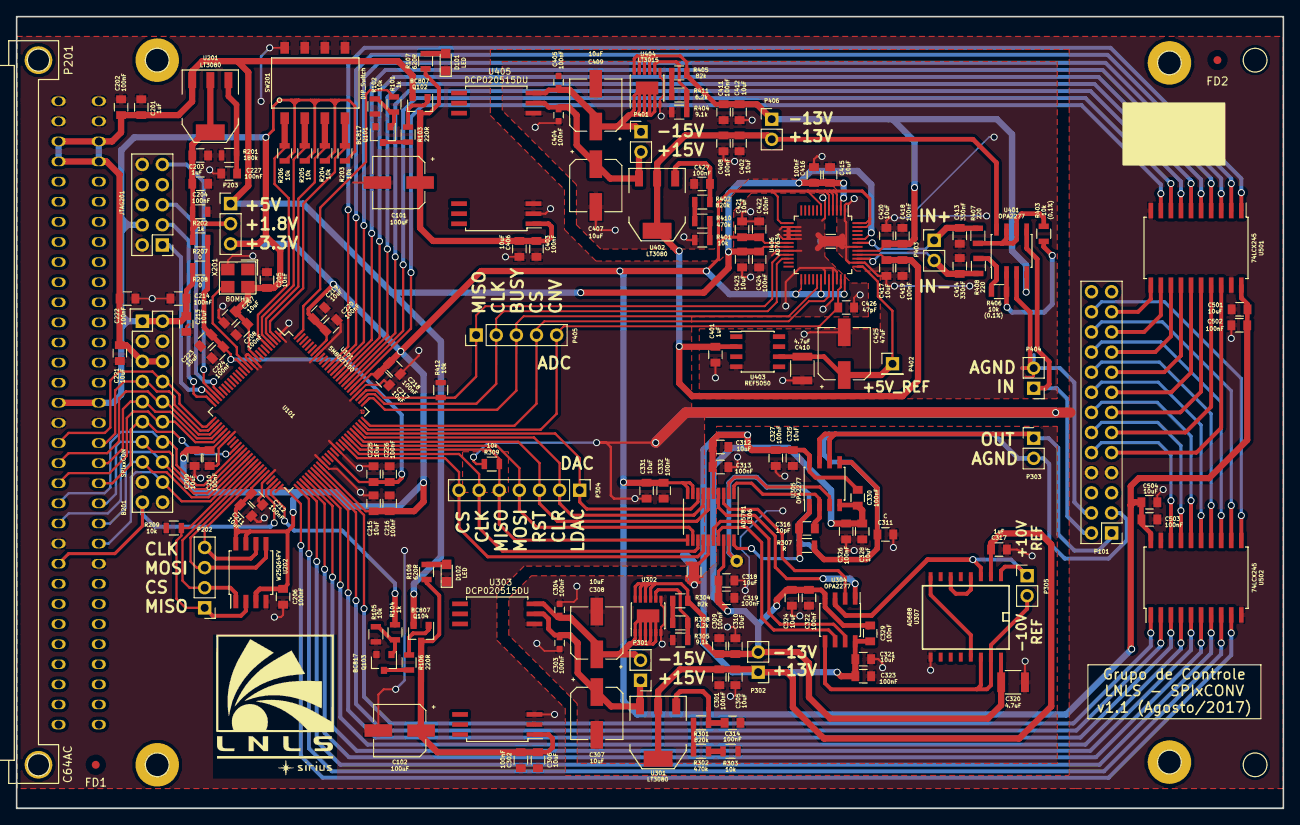
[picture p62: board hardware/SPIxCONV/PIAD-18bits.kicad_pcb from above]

Board: 2 copper layers, 160.0 x 100.0 mm, 178 parts (0 on the bottom side), 130 nets.

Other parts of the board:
FD1, FD4: Fiducial_1mm_Dia_2.54mm_Outer_CopperBottom
FD2, FD3: Fiducial_1mm_Dia_2.54mm_Outer_CopperTop

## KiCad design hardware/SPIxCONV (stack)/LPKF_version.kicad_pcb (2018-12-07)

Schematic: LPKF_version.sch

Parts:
Beagle101: BeagleBone; BEAGLEBONEBLACK
P101: CONN_01X05; Pin_Header_Straight_1x05_Pitch2.54mm
P102: CONN_01X07; Pin_Header_Straight_1x07_Pitch2.54mm
P103: CONN_02X02; Pin_Header_Straight_2x02_Pitch2.54mm
P104, P105, P106, P107: CONN_01X01; ground_plane_via
P108: CONN_01X02; Pin_Header_Straight_1x02_Pitch2.54mm
P109: CONN_01X01; Pin_Header_Straight_1x01_Pitch2.54mm
U101, U102: HC245; SOIC-20W_7.5x12.8mm_Pitch1.27mm

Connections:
/+5V: Beagle101.C5, Beagle101.C6, P108.1, P108.2, U101.20, U102.20
/ADC_BUSY: P101.3, U102.7
/ADC_CLK: P101.2, U102.8
/ADC_CNV: P101.5, U102.5
/ADC_CS: P101.4, U102.6
/ADC_MISO: P101.1, U102.9
/DAC_CLK: P102.6, U101.3
/DAC_CLR: P102.2, U101.7
/DAC_CS: P102.7, U101.2
/DAC_LDAC: P102.1, U101.8
/DAC_MISO: P102.5, U101.4
/DAC_MOSI: P102.4, U101.5
/DAC_RST: P102.3, U101.6
/GPIO_BUSY: Beagle101.C16, U102.13
/GPIO_CLR: Beagle101.C25, U101.13
/GPIO_CNV: Beagle101.C14, U102.15
/GPIO_LDAC: Beagle101.C24, U101.12
/GPIO_RST: Beagle101.C26, U101.14
/PWR_SYS: Beagle101.C23, P109.1
/SPI0_CS: Beagle101.C17, U102.14
/SPI0_MISO: Beagle101.C18, U102.11
/SPI0_SCLK: Beagle101.C22, U102.12
/SPI1_CS0: Beagle101.C28, U101.18
/SPI1_MISO: Beagle101.C30, U101.16
/SPI1_MOSI: Beagle101.C29, U101.15
/SPI1_SCLK: Beagle101.C31, U101.17
GND: Beagle101.C1, Beagle101.C2, Beagle101.C43, Beagle101.C44, Beagle101.C45, Beagle101.C46, P103.1, P103.2, P103.3, P103.4, U101.1, U101.10, U101.19, U102.1, U102.10, U102.19

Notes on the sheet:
SPI0: ADC SPI1: DAC

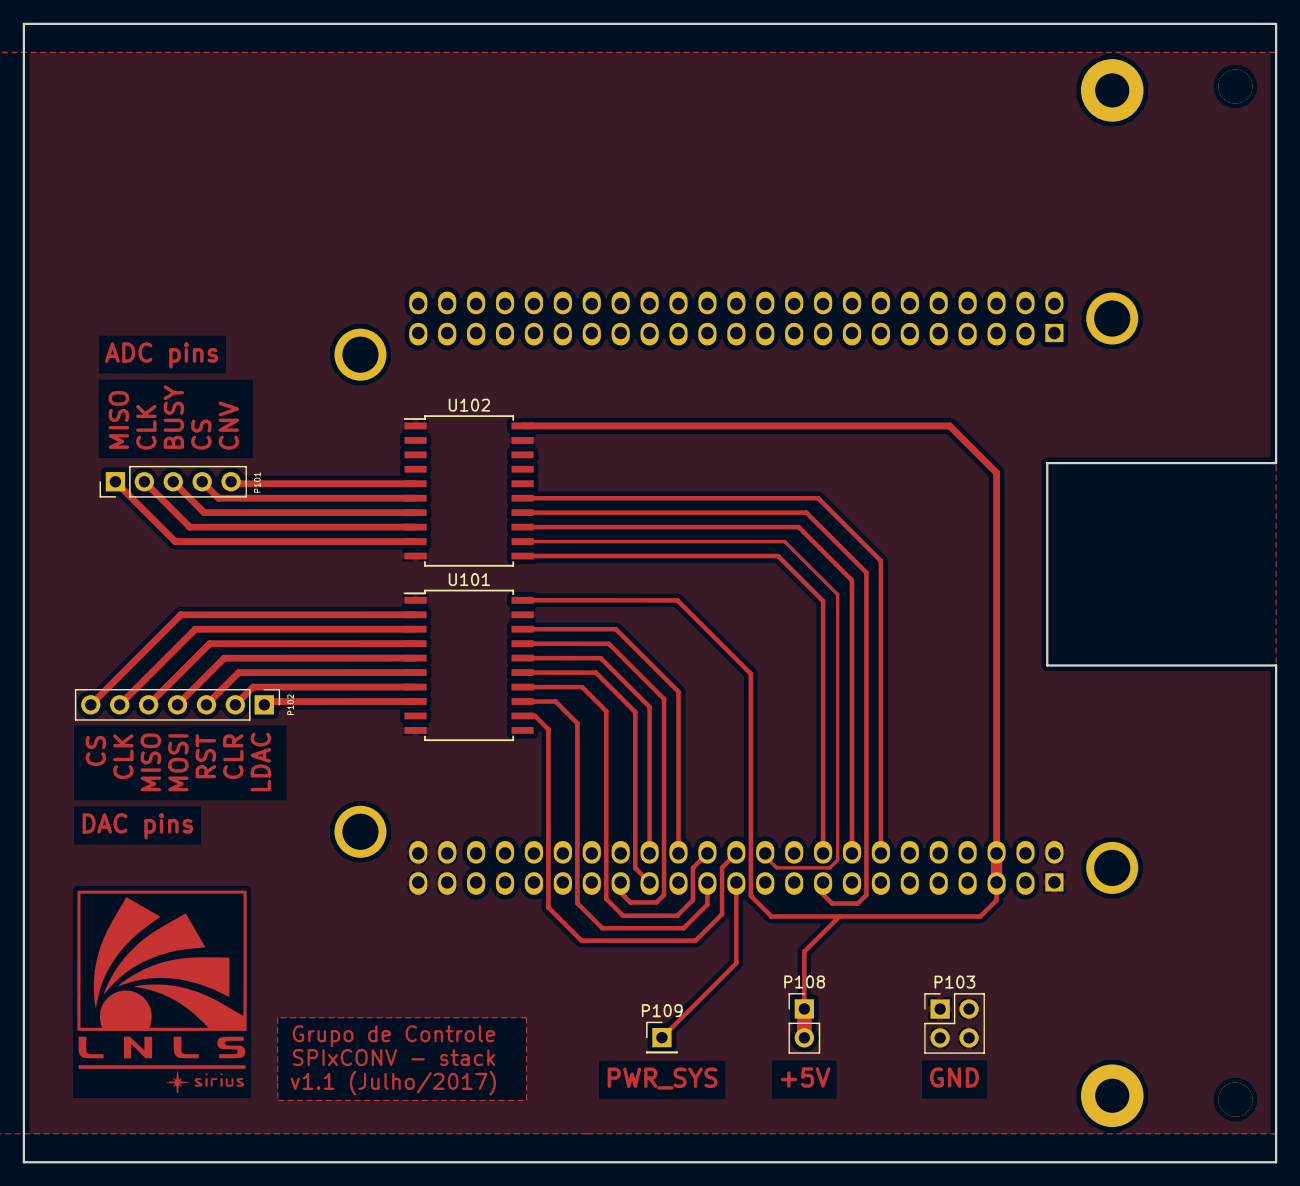
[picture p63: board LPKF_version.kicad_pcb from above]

Board: 2 copper layers, 110.0 x 100.0 mm, 13 parts (1 on the bottom side), 27 nets.

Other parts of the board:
P102#2: CONN_01X07; LNLS_LOGO_Silk

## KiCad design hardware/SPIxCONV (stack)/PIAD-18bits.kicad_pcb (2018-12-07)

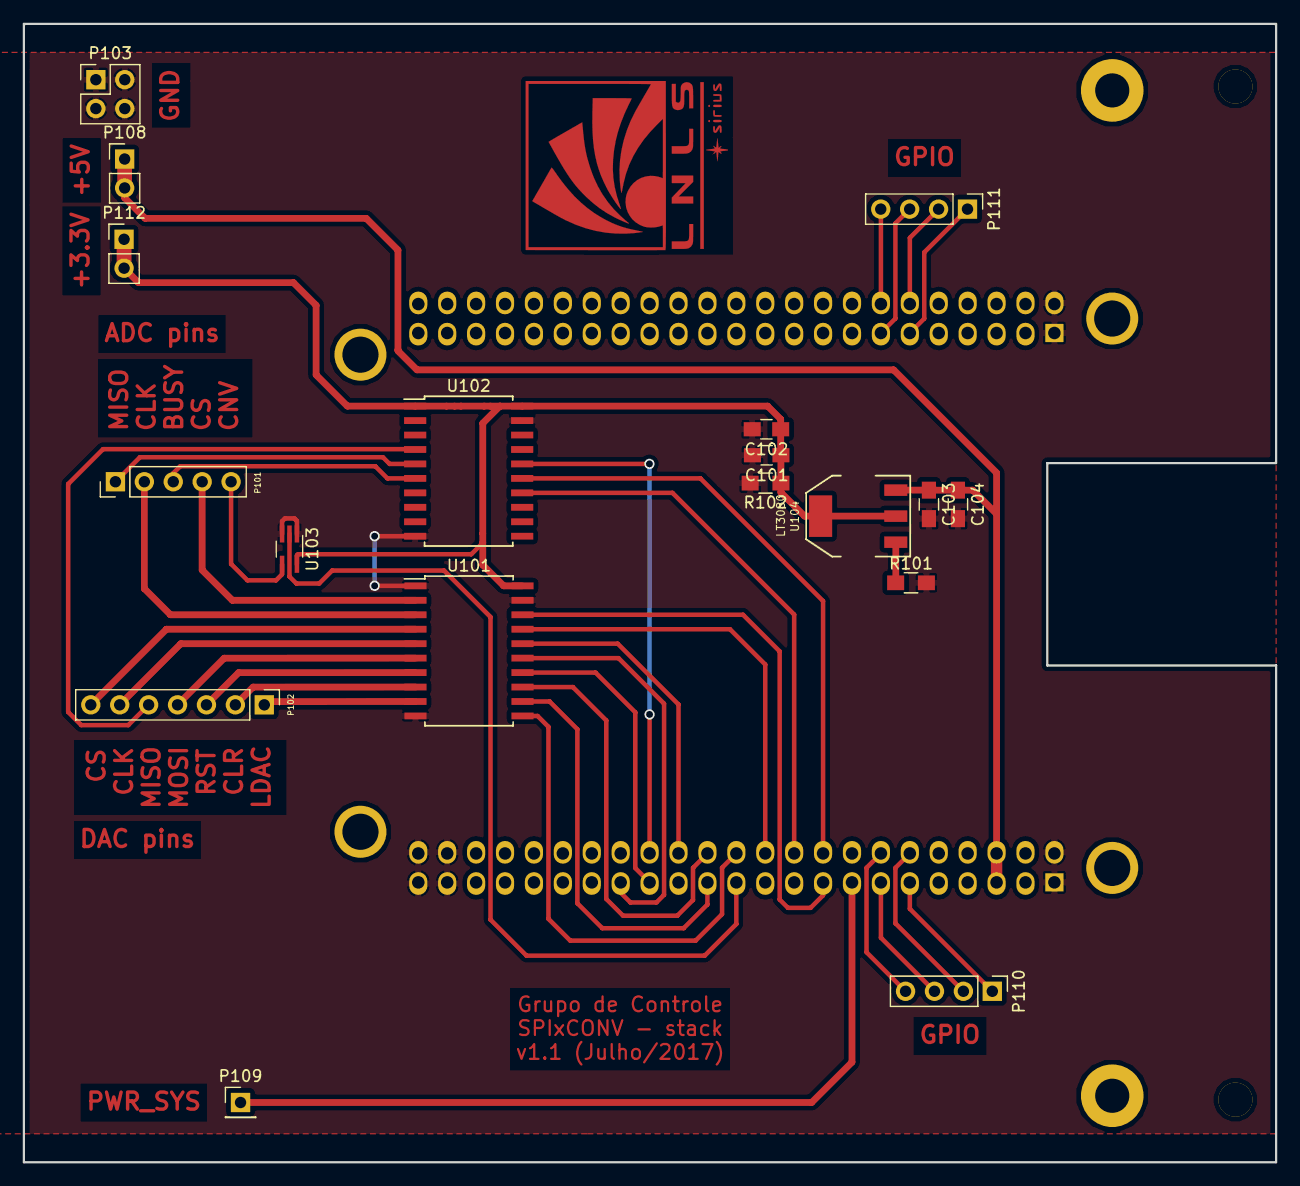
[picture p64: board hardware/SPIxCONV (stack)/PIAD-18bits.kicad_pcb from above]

Board: 2 copper layers, 110.0 x 100.0 mm, 24 parts (1 on the bottom side), 36 nets.

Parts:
Beagle101: BeagleBone; BEAGLEBONEBLACK
C101, C103: 1uF; C_0805_HandSoldering
C102, C104: 100nF; C_0805_HandSoldering
P101: CONN_01X05; Pin_Header_Straight_1x05_Pitch2.54mm
P102: CONN_01X07; Pin_Header_Straight_1x07_Pitch2.54mm
P102#2: CONN_01X07; LNLS_LOGO_Silk
P103: CONN_02X02; Pin_Header_Straight_2x02_Pitch2.54mm
P104, P105, P106, P107: CONN_01X01; ground_plane_via
P108, P112: CONN_01X02; Pin_Header_Straight_1x02_Pitch2.54mm
P109: CONN_01X01; Pin_Header_Straight_1x01_Pitch2.54mm
P110, P111: CONN_01X04; Pin_Header_Straight_1x04_Pitch2.54mm
R101: 330k; R_0805_HandSoldering
R102: 1k; R_0805_HandSoldering
U101, U102: 74LCX245; SOIC-20W_7.5x12.8mm_Pitch1.27mm
U103: 74LS125; SOT-353_SC-70-5_Handsoldering
U104: LT3080; SOT-223

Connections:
/+3.3V: C101.1, C102.1, P112.1, P112.2, R102.1, U101.20, U102.1, U102.20, U104.2, U104.4
/+5V: Beagle101.C5, Beagle101.C6, C103.1, C104.1, P108.1, P108.2, U104.3
/ADC_BUSY: P101.3, U102.6
/ADC_CLK: P101.2, U101.3
/ADC_CS: P101.4, U101.2
/ADC_MISO: P101.1, U102.5
/DAC_CLK: P102.6, U101.5
/DAC_CLR: P102.2, U101.8
/DAC_CS: P102.7, U101.4
/DAC_LDAC: P102.1, U101.9
/DAC_MISO: P102.5, U102.4
/DAC_MOSI: P102.4, U101.6
/DAC_RST: P102.3, U101.7
/GPIO_0: Beagle101.C11, P110.1
/GPIO_1: Beagle101.C12, P110.2
/GPIO_2: Beagle101.C13, P110.3
/GPIO_3: Beagle101.C14, P110.4
/GPIO_4: Beagle101.B11, P111.1
/GPIO_5: Beagle101.B12, P111.2
/GPIO_6: Beagle101.B13, P111.3
/GPIO_7: Beagle101.B14, P111.4
/GPIO_BUSY: Beagle101.C20, U102.14
/GPIO_CLR: Beagle101.C25, U101.12
/GPIO_CNV: Beagle101.C23, U103.2
/GPIO_LDAC: Beagle101.C24, U101.11
/GPIO_RST: Beagle101.C26, U101.13
/PWR_SYS: Beagle101.C15, P109.1
/SPI0_CS: Beagle101.C17, U101.18
/SPI0_MISO: Beagle101.C18, U102.15
/SPI0_SCLK: Beagle101.C22, U101.17
/SPI1_CS0: Beagle101.C28, U101.16
/SPI1_MISO: Beagle101.C30, U102.16
/SPI1_MOSI: Beagle101.C29, U101.14
/SPI1_SCLK: Beagle101.C31, U101.15
GND: Beagle101.B1, Beagle101.B2, Beagle101.C1, Beagle101.C2, Beagle101.C43, Beagle101.C44, Beagle101.C45, Beagle101.C46, C101.2, C102.2, C103.2, C104.2, P103.1, P103.2, P103.3, P103.4, R101.2, R102.2, U101.1, U101.10, U101.19, U102.10, U102.19, U103.1, U103.3
unnamed: R101.1, U104.1

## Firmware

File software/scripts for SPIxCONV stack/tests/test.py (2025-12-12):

#!/usr/bin/python3

from Adafruit_BBIO.SPI import SPI
import Adafruit_BBIO.GPIO as GPIO
import time
#-------------------------------------------------------
# initialize the bus and device /dev/spidev1.0
spi0 = SPI(0,0)     #ADC
# initialize the bus and device /dev/spidev2.0
spi1 = SPI(1,0)     #DAC
#-------------------------------------------------------
#Set the maximum clock frequency
spi0.msh=100000
spi1.msh=100000
#-------------------------------------------------------
# mnemonics for GPIO
RST = "P9_26"
CLR = "P9_25"
LDAC = "P9_24"
BUSY = "P9_20"
CNV = "P9_23"
PWR_SYS = "P9_16"
#PWR_SYS = "P9_15"
#-------------------------------------------------------
# defining outputs
GPIO.setup(RST, GPIO.OUT)
GPIO.setup(CLR, GPIO.OUT)
GPIO.setup(LDAC, GPIO.OUT)
GPIO.setup(CNV, GPIO.OUT)
GPIO.setup(PWR_SYS, GPIO.OUT)
#-------------------------------------------------------
# defining inputs
GPIO.setup(BUSY, GPIO.IN)
#-------------------------------------------------------
# initialization of outputs
GPIO.output(RST, GPIO.LOW)
GPIO.output(CLR, GPIO.LOW)
GPIO.output(LDAC, GPIO.LOW)
GPIO.output(CNV, GPIO.LOW)
GPIO.output(PWR_SYS, GPIO.LOW)
#=======================================================
#	pinout for DAC and ADC bus
#=======================================================
'''
DAC pins
	SPI1_CS:	"P9_28"
	SPI1_SCLK:	"P9_31"
	SPI1_MOSI:	"P9_29"
	SPI1_MISO:	"P9_30"
	GPIO_RST:	"P9_26"
	GPIO_CLR:	"P9_25"
	GPIO_LDAC:	"P9_24"

ADC pins
	SPI0_CS:	"P9_17"
	SPI0_SCLK:	"P9_22"
	SPI0_MISO:	"P9_18"
	GPIO_BUSY:	"P9_20"
	GPIO_CNV:	"P9_23"

GPIO pins
	GPIO_0: "P9_11"
	GPIO_1: "P9_12"
	GPIO_2: "P9_13"
	GPIO_3: "P9_14"

	GPIO_4: "P8_11"
	GPIO_5: "P8_12"
	GPIO_6: "P8_13"
	GPIO_7: "P8_14"

POWER SYSTEM:
	PWR_SYS = "P9_16"
'''
#=======================================================
#	testing SPI
#=======================================================

while(1):
	# RST = 1 --> address
#	GPIO.output(RST, GPIO.HIGH)
#	time.sleep(0.001)
	# RST = 0 --> slaves
#	GPIO.output(RST, GPIO.LOW)
#	time.sleep(0.001)

	# send data through SPI
	spi1.writebytes([0x20, 0x03, 0x12])
	spi0.writebytes([0x02, 0x30, 0x21])

#	GPIO.output(PWR_SYS, GPIO.HIGH)
#	GPIO.output(RST, GPIO.HIGH)
#	GPIO.output(CLR, GPIO.HIGH)
#	GPIO.output(LDAC, GPIO.HIGH)
#	GPIO.output(CNV, GPIO.HIGH)

#	GPIO.output(PWR_SYS, GPIO.LOW)
#	GPIO.output(RST, GPIO.LOW)
#	GPIO.output(CLR, GPIO.LOW)
#	GPIO.output(LDAC, GPIO.LOW)
#	GPIO.output(CNV, GPIO.LOW)

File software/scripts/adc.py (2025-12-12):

#!/usr/bin/python3

from Adafruit_BBIO.SPI import SPI
import Adafruit_BBIO.GPIO as GPIO
#-------------------------------------------------------
import selection
import math
import dac
import time
import flash
# initialize the bus and device /dev/spidev1.0
spi = SPI(0,0)
# global variables
global GAIN
global OFFSET
GAIN = 1
OFFSET = 0
# mnemonics for GPIO
BUSY = "P8_37"
CNVST = "P9_24"    #DIO3
# defining outputs
GPIO.setup(CNVST, GPIO.OUT)
# defining inputs
GPIO.setup(BUSY, GPIO.IN)
# initialization of outputs
GPIO.output(CNVST, GPIO.HIGH)
#=======================================================
#    Power on ADC circuit
#=======================================================
def on(board):
    selection.decoder(board)
    # put PWR_GOOD_ADC to "1"
    spi.writebytes([0x02])
    selection.clk_ff(board)
    #------------------------
    # read calibration parameters
    global GAIN, OFFSET
    GAIN = flash.adc_gain_read(board)
    OFFSET = flash.adc_offset_read(board)
    if math.isnan(GAIN):
        GAIN = 1.0
    if math.isnan(OFFSET):
        OFFSET = 0.0
#=======================================================
#    Power off ADC circuit
#=======================================================
def off(board):
    selection.decoder(board)
    # put PWR_GOOD_ADC to "1"
    spi.writebytes([0x03])
    selection.clk_ff(board)
#=======================================================
#    Power off all ADC circuits (from board 0 to 7)
#=======================================================
def off_all():
    for board in range(8):
        selection.decoder(board)
        # put PWR_GOOD_ADC to "1"
        spi.writebytes([0x03])
        selection.clk_ff(board)
#=======================================================
#                  ADC Calibration
#=======================================================
# this function runs an ADC calibration for the selected board
# DAC should be already calibrated for this calibration
# it runs a stability test for two different set points
# the mean of this two points are used as a reference
# for the calibration.
def calibration(board):
    # global variables
    global GAIN, OFFSET
    # turns on DAC and ADC circuit
    dac.on(board)
    on(board)
    # reset previous Calibration
    GAIN = 1
    OFFSET = 0
    # set up DAC
    selection.dac(board)
    dac.config(board)

    calibration = [-9, 9]
    total_measures = 10000
    # defining variables for MAX, MIN and MEAN (ADC measure)
    min_adc = [0] * 5
    max_adc = [0] * 5
    mean_adc = [0] * 5
    std_var = [0] * 5
    i = 0
    j = 0
    ############################################################
    interval = []
    for x in calibration:
        measure = []
        #print("  ============================================================================")
        #print("  |                           CALIBRATION:                                   |")
        #print("  ============================================================================")

        # select DAC and write correspondent value
        base = int(((x+10)/(20/float(262144))))
        interval.append(base)
        selection.dac(board)
        dac.write(base)
        time.sleep(60)
        measure = []
        for i in range (total_measures):
            selection.adc(board)
            adc_value = read()
            measure.append(adc_value)
            # check if it is the first measure
            if(i == 0):
                min_adc[j] = measure[0]
                max_adc[j] = measure[0]
                mean_adc[j] = measure[0]*1.0
            # if not, calculate max, min and mean
            else:
                if(measure[i] < min_adc[j]):
                    min_adc[j] = measure[i]
                if(measure[i] > max_adc[j]):
                    max_adc[j] = measure[i]
                mean_adc[j] = (mean_adc[j]*i + measure[i])/(i + 1)
            i += 1
            adc_volt = float(adc_value)/262143*20-10
            adc_volt_str = str(adc_volt)
            adc_volt_str = adc_volt_str[0:adc_volt_str.find(".")+8]
            #sys.stdout.write("  | " + str(adc_value) + "\t" + str(adc_value) + "\t\t\t\t\t\t\t" + "|" + "\n")
        j += 1
    REFERENCE = mean_adc[0]
    # calculating gain correction
    theoretical_step = 20.0 / 262143
    calibrated_step = 18.0 / (mean_adc[1] - mean_adc[0])
    GAIN = calibrated_step / theoretical_step
    # calculating offset correction (around code 131072, 0V)
    interval = 9.0 / theoretical_step
    OFFSET = 131072 - interval - mean_adc[0]
    # update OFFSET taking in account REFERENCE value:
    OFFSET = REFERENCE * (1 - GAIN) + OFFSET
    # store both parameters (GAIN and OFFSET) in flash memory
    flash.adc_gain_write(board, GAIN)
    flash.adc_offset_write(board, OFFSET)
    # return two parameters: gain and offset
    #output = [GAIN, OFFSET]
    print("\tgain = " + str(GAIN))
    print("\toffset = " + str(OFFSET))
    #return output
#---------------------------------------------------------------------
def read_calibration(board):
    global GAIN, OFFSET
    # global variables
    GAIN = flash.adc_gain_read(3)
    OFFSET = flash.adc_offset_read(3)
    print("\tgain = " + str(GAIN))
    print("\toffset = " + str(OFFSET))
#=======================================================
#    read a value in DAC (value in binary code)
#=======================================================
def read(adc_gain=None, adc_offset=None):
    # global variables
    global GAIN, OFFSET
    if adc_gain is None:
        adc_gain = GAIN
    if adc_offset is None:
        adc_offset = OFFSET
    # CNVST = 0 --> start conversion
    GPIO.output(CNVST, GPIO.LOW)
    #################################
    # wait for the rising of BUSY
    #################################
    #while(GPIO.input(BUSY) == 0):
    #    pass # does nothing
    # delay of 1us
    #time.sleep(0.1)
    #--------------------------------
    # bring CNVST back to "1" state
    GPIO.output(CNVST, GPIO.HIGH)
    #################################
    # wait for the falling of BUSY (end of conversion)
    #################################
    #while(GPIO.input(BUSY) == 1):
    #    pass
    #--------------------------------

    # read data from ADC
    #data = spi.readbytes(1)
    #adc = data[0]
    #adc = adc << 8

    #data = spi.readbytes(1)
    #data = data[0]
    #adc += data
    #adc = adc << 8

    #data = spi.readbytes(1)
    #data = data[0]
    #adc += data
    #adc = adc >> 6

    data = spi.readbytes(3)
    adc = (data[0] << 10) + (data[1] << 2) + (data[2] >> 6)
    # applying GAIN and OFFSET corretion
    adc = int(round(adc * adc_gain + adc_offset))
    if (adc < 0):
        adc = 0
    elif (adc > 262143):
        adc = 262143
    return adc
#=======================================================
#    read a value in DAC (value in Volts)
#=======================================================
def readVolts():
    adc = read()*1.0
    adc = (adc/262143)*20 - 10
    adc = round(adc, 6)
    return adc
#=======================================================
#    read ADC many times and calculate a mean
#=======================================================
def mean(value, adc_gain=None, adc_offset=None):
    # global variables
    global GAIN, OFFSET
    if adc_gain is None:
        adc_gain = GAIN
    if adc_offset is None:
        adc_offset = OFFSET

    # defining variables for MAX, MIN and MEAN (ADC measure)
    measure = []
    min_adc = 0
    max_adc = 0
    mean_adc = 0.0
    i = 0
    #-------------------------------------------------------
    while(i < value):
        adc = read()
        #adc_print(adc)
        measure.append(adc)
        # calculate ADC min, max and mean values
        # setting first values
        if(i == 0):
            min_adc = adc
            max_adc = adc
            mean_adc = float(adc)
        else:
            if(adc < min_adc):
                min_adc = adc
            if(adc > max_adc):
                max_adc = adc
            mean_adc = (mean_adc*i + adc)/(i + 1)
        i += 1
    #-------------------------------------------------------
    #calculate standard deviation
    diff = measure
    diff[:] = [x - mean_adc for x in measure]
    diff_square = [x**2 for x in diff]
    std_var = sum(diff_square)/(len(measure)*1.0)
    std_var = math.sqrt(std_var)
    std_var = "{0:.3f}".format(std_var)
    #mean_adc = "{0:.2f}".format(mean_adc)
    #mean_adc = float(mean_adc)
    #-------------------------------------------------------
    diff = max_adc - min_adc
    #mean_adc = int(round(mean_adc * GAIN + OFFSET, 2))
    mean_adc = round(mean_adc * adc_gain + OFFadc_offsetSET, 2)
    return [std_var, diff, mean_adc, min_adc, max_adc]
'''
    print("\nnumber of measures = " + str(value))
    print("standard variation = " + std_var)
    print("width of histogram = " + str(diff))
    print("mean = " + mean_adc)
    print("minimum = " + str(min_adc))
    print("maximum = " + str(max_adc) + "\n")
'''
#=======================================================
#    read ADC many times and calculate a mean in Volts
#=======================================================
def meanVolts(value):
    adc = mean(value)
    adc = adc[2]
    adc = (adc/262143)*20 - 10
    adc = round(adc, 6)
    return adc

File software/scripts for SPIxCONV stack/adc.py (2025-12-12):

#!/usr/bin/python3

from Adafruit_BBIO.SPI import SPI
import Adafruit_BBIO.GPIO as GPIO
import math
import time
import dac
#-------------------------------------------------------
# initialize the bus and device /dev/spidev1.0
spi0 = SPI(0,0)
#defining mode (CPOL = 0; CPHA = 1)
spi0.mode = 1
#defining speed (in bps)
spi0.msh = 10000000
#-------------------------------------------------------
# mnemonics for GPIO
BUSY = "P9_20"
CNV = "P9_23"
#-------------------------------------------------------
# defining outputs
GPIO.setup(CNV, GPIO.OUT)
#-------------------------------------------------------
# defining inputs
GPIO.setup(BUSY, GPIO.IN)
#-------------------------------------------------------
# initialization of outputs
GPIO.output(CNV, GPIO.LOW)
#=======================================================
#    ADC calibration parameters
#=======================================================
# global variables
global GAIN
global OFFSET
global REFERENCE
#REFERENCE = 13107
#GAIN = 1
#OFFSET = 0
REFERENCE = 13140.5627
GAIN = 1.00043749802
OFFSET = -32.9127
#=======================================================
#    read a value in DAC (value in binary code)
#=======================================================
def read():
    # global variables
    global REFERENCE, GAIN, OFFSET
    # CNVST = 0 --> start conversion
    GPIO.output(CNV, GPIO.LOW)
    #################################
    # wait for the rising of BUSY
    #################################
    #while(GPIO.input(BUSY) == 0):
    #    pass # does nothing
    # delay of 1us
    #time.sleep(0.1)
    #--------------------------------
    # bring CNVST back to "1" state
    GPIO.output(CNV, GPIO.HIGH)
    #################################
    # wait for the falling of BUSY (end of conversion)
    #################################
    #while(GPIO.input(BUSY) == 1):
    #    pass
    #--------------------------------

    # read data from ADC
    #data = spi0.readbytes(1)
    #adc = data[0]
    #adc = adc << 8

    #data = spi0.readbytes(1)
    #data = data[0]
    #adc += data
    #adc = adc << 8

    #data = spi0.readbytes(1)
    #data = data[0]
    #adc += data
    #adc = adc >> 6

    data = spi0.readbytes(3)
    adc = (data[0] << 10) + (data[1] << 2) + (data[2] >> 6)
    # applying GAIN and OFFSET corretion
    adc = int(round((adc - REFERENCE) * GAIN + OFFSET + REFERENCE))
    return adc
#=======================================================
#    read a value in DAC (value in Volts)
#=======================================================
def readVolts():
    adc = read()*1.0
    adc = (adc/262143)*20 - 10
    adc = round(adc, 6)
    return adc
#=======================================================
#    read ADC many times and calculate a mean
#=======================================================
def mean(value):
    # defining variables for MAX, MIN and MEAN (ADC measure)
    measure = []
    min_adc = 0
    max_adc = 0
    mean_adc = 0.0
    i = 0
    #-------------------------------------------------------
    while(i < value):
        adc = read()
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

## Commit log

2018-12-07 SPIxCONV project cloned from LNLS internal git server
    [ADC.sch, Boards information (location, calibration parameters, etc).ods, CPLD_SPIxxCON.sch, DAC.sch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]
2019-03-06 changed executable permission of config-pin
2019-03-06 pinout documentation review
    [SPIxCONV pinout connector.ods]
2019-03-06 PyDM ui displays added
    [SPIxCONV board link connector.ods, SPIxCONV interface connector.ods]
2019-05-14 ADC measure returning maximum of 10 last samples
2019-10-07 added multiple devices displays
2020-01-06 Support for python3
    Python2 will be deprecated. Changes on "print" commands!
2020-01-28 removed board address ID dependency (requirement: one BBB for each SPIxCONV)
2020-02-04 fixed board address detection bug
2020-02-04 uncommented board_address argument
2020-02-04 discarded board ID (data[0]) information sent by IOC
2020-02-04 discarded args.board_address information from config
2020-07-13 [voltage-adjustment] queue architecture adopted
2020-07-13 [voltage-adjustment] voltage adjustment commands queue added
2020-07-13 [pulse-sts] pin direction configured
2020-07-13 [voltage-adjustment] fields added to DAC output message (voltage factor, step trigger and delay)
2020-07-14 [voltage-adjustment] fixed fields in DAC output message
2020-07-15 [voltage-adjustment] voltage steps implemented
2020-07-15 [voltage-RB] voltage RB measure at IOC initialization
2020-07-15 [voltage-adjustment] started fix for power PS on with setpoint
2020-07-16 [voltage-adjustment] finished fix for power PS on with setpoint
2020-07-16 [voltage-adjustment] removed print line
2020-07-16 [voltage-adjustment] check last voltage setpoint at code initialization
2020-07-16 [voltage-adjustment] use PwrState-Sel instead of PwrState-Sts for algorithm
2020-07-22 [voltage-steps] included hostname support to initialize steps vars
2020-07-22 [voltage-steps] removed rule to adjust setpoint directly if PS is off
2020-07-22 [voltage-steps] check if SP is equal to RB
2020-07-22 [voltage-steps] last_setpoint fix
2020-07-22 [voltage-steps] last_setpoint initialization
2020-07-22 [voltage-steps] included debug logs for voltage adjustment
2020-07-22 [voltage-steps] changed log level from debug to info
2020-07-22 [voltage-steps] logs added
2020-07-22 [voltage-steps] logs related to hostname added
2020-07-22 [voltage-steps] ensure RB is equal to RB
2020-07-22 [voltage-steps] send SP to RB
2020-07-27 [voltage-steps] added try/except for threads 2 and 3
2020-07-27 [voltage-steps] changed identifier from hostname to ip address
2020-07-27 [voltage-steps] included steps var in identifier
2020-07-27 [voltage-steps] started using terminator for messages (CR+LF)
2020-07-29 [voltage-adjustment] removed print and added terminator characters (CR+LF)
2020-07-29 [voltage-adjustment] lock support to avoid race conditions included
2020-07-30 [voltage-adjustment] changed logs setpoint unit (from code to voltage)
2020-07-30 [voltage-adjustment] included step number in logs (for gradual adjustments)
2020-07-30 [voltage-adjustment] restored rule to stop gradual adjustments if a new setpoint is received
2020-07-30 [voltage-adjustment] PS on/off & Pulse on/off logs included
2020-07-30 [voltage-adjustment] added logs to write commands
2020-07-30 [voltage-adjustment] adjusted logs
2020-07-31 [voltage-adjustment] changed line split method (break only CR+LF)
2020-07-31 [voltage-adjustment] changed command 0x0D to 0x11
2020-09-15 [readme] cut figures and added them to readme
2020-09-15 [readme] pcb figs and link to github-page added
2020-09-16 connectors figure added
2020-09-16 [readme] connectors image added
2020-09-16 [readme] GPIO expander board info added
2020-09-16 [readme] main board and gpio stack added
2020-09-17 [readme] main board image added
2020-09-17 [readme] CPLD pinout added
    [SPIxCONV pinout connector.ods]
2020-09-18 figure rotated (main board)
2020-09-18 main board figures rotated
2020-09-21 [readme] main board division figures added
2020-09-21 [readme] main board: testpoints figures added
2020-09-21 [readme] main board division updated
2020-09-23 [documentation] fixed typo in CPLD connector figure
2020-09-23 [documentation] figures of interface connectors in GPIO stack updated
2020-09-23 [readme] add boards identification
2020-09-23 [readme] add calibration figures
2020-09-23 [readme] main board testpoint section created
2020-09-23 [documentation] figures updated (rotated, cut, divison redone)
2020-09-23 [readme] voltmeter datasheet added and calibration section updated
2020-09-23 [readme] add calibration data
    [Boards information (location, calibration parameters, etc).ods]
2020-09-23 [readme] fixed calibration data table
2021-03-19 Added analog feedback project
    [Adapter.kicad_pcb, Adapter.sch]
2021-09-30 Redis script for Voltage Feedback
2023-02-08 Updates for reading 3 boards
2023-02-14 removing prints
2023-09-05 Removing print from dacpy, reducing SPI BR and config NLK hostname
2023-11-13 Update spixconv_unix_socket.py
    Add a `time.sleep` for waiting for next setpoint instead of checking if queue is not empty (mandatory for use with more than one board)
2024-03-06 spixconv_socket.py: add keepalive option for socket connection
    Prevents unknown broken connections
2024-09-05 spixconv_socket.py: remove print
2025-08-07 Add structured response format to socket protocol (no checksum)
    Updated the communication protocol to include explicit command
    tracking in responses. Each reply now follows the format:
    `[command][status][data]\r\n`
    The status byte is currently hardcoded to 0x01 (success).
    The checksum field, previously part of the response format,
    was removed in a prior commit and will be reintroduced in a future
    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
2025-08-18 Refactor functions out of `if __name__ == '__main__'` block
    Move `voltage_steps`, `voltage_adjustment`, `read_from_list` and
    `write_to_list` outside the main block. Made `queue_general`,
    `queue_voltage` and `args` global for accessibility.
2025-08-20 Update IOC protocol file
    Add the current version of the .proto file being used in the IOC.
    This updated protocol file matches the more informative header
    (`[command][status][data]\r\n`) discussed in previous commits.
    Also, this new header provides a mismatch handler that is
    responsible for detecting and handling out-of-sync messages,
    ensuring proper synchronization between the IOC and BeagleBone.
2025-11-06 Fix `print` syntax
2025-11-06 Handle bytes/strings correctly in `spixconv_unix_socket.py`
    Update socket handling in `spixconv_unix_socket.py` for Python 3
    compatibility. All received data is now treated as `bytes`, with
    proper decoding when converting to integers and encoding when
    sending responses. Replaces `ord()` and `int()` on `str` with
    appropriate `bytes` handling.
2025-11-06 Further bytes/strings adjustments in `spixconv_unix_socket.py`
    Additional fixes to Python 3 compatibility, ensuring all socket
    data is handled consistently and decoding/encoding is robust.
2025-12-12 Document Updated Bit Usage: Pulse-Sts and New Interlock 9 Assignment
    This commit updates the documentation files, specifically the .ods spreadsheet and the
    rendered .jpeg figure, to reflect two changes in bit usage within the IOC B-A connector
    interface. First, it documents that bit B4 (pin 18) is used for reading the Trigger
    Pulse status (Pulse-Sts) from the source. Second, it records the assignment of
    Interlock 9 to bit B5 (pin 20), which was previously unused.
    [SPIxCONV pinout connector.ods]
2025-12-16 Remove IOC files
    Removing IOC files because they are mirrored from production and can easily go out of sync. We’ll document the authoritative location instead to avoid duplication.
